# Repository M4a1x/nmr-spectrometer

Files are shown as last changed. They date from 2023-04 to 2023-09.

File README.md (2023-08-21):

<div align="center">
  <a href="" rel="noopener">
 BioNMR Group Logo</a>
</div>

<div align="center">Building a 25MHz NMR spectrometer<br \>01.04.2023 - 30.09.2023</div>

<div align="center">

  []() 
  

</div>

---

<div align="center"> magnETHical is a simple low-cost low-field 0.6T NMR spectrometer based on a RedPitaya and custom hardware. This repository contains everything to build your own. This includes simulations, specifications, full hardware descriptions and CAD designs, Python control code and reproducible measurement results.
</div>

## 📝 Table of Contents
- [📝 Table of Contents](#-table-of-contents)
- [🧐 About ](#-about-)
- [🏁 Getting Started ](#-getting-started-)
  - [✅ Prerequisites](#-prerequisites)
  - [🔧 Hardware](#-hardware)
  - [🖥️ Software](#️-software)
- [⚙️ Running the tests ](#️-running-the-tests-)
- [🧪 Usage ](#-usage-)
- [⛏️ Built Using ](#️-built-using-)
- [✍️ Authors ](#️-authors-)
- [🎉 Acknowledgements ](#-acknowledgements-)

## 🧐 About 
Since the discovery of the Zeeman effect in 1896 and its first use for spectroscopy in the 1940s a lot of technological advancements enabled the capture of increasingly better spectrums and the development of increasingly advanced techniques. Unfortunately, this advancement isn't cheap. Modern NMR spectroscopes cost a fortune, limiting access to this technology to well-funded research institutes, keeping out institutes from the southern hemisphere and limiting its exposure.

magnETHical seeks to provide a low-cost low-field NMR system not only capable of relaxometry but also spectroscopy for a price about an order of magnitude lower than existing devices. It's an open-source well-documented system that can be fully assembled in-house and consists of flexible components that are easily and readily available. 90% of the current ~10k€ price tag is comprised of the magnet with room for at least halving the price in the foreseeable future.

This repository seeks to provide everything needed to order, assemble and operate your own magnETHical NMR spectrometer.

## 🏁 Getting Started 

### ✅ Prerequisites
Great care has been taken to only use widely available free and open-source software so that this project may be built by anyone without any software licensing fees.

Throughout this README and the linked READMEs below a basic familiarity with the used software is assumed. However, anyone with some time on their hands should be able to follow them without much trouble after a very basic introduction to these programs. If you have trouble understanding any of the instructions, please feel free to open an issue - it's likely an error in this documentation and not on your side.

### 🔧 Hardware
The hardware consists of five main parts
- the [magnet](),
- the [digital signal generation, reception and processing board](),
- the [analogue amplification board](),
- the [electrical shimming system]() and
- the [NMR probe]().

Each of these parts can be built, assembled and verified independently of each other. For instructions on building these sub-systems, see the respective READMEs linked in the list above.

With all parts built, the final system needs to be assembled according to the following schematic.

![Block diagram of the different high-level parts of the spectrometer]()

The final assembly then looks something like this

![Picture of the final measurement setup]()

### 🖥️ Software
Having built the hardware above the [Python control software]() can be used to capture spectra. See the linked article for a detailed guide on how to set up the software. We recommend a dedicated computer setup to run the experiments.

## ⚙️ Running the tests 
The simplest test is running marcos test without/with water. measure coil ringing

Explain how to run the automated tests for this system.

## 🧪 Usage 
To record spectra...

How to use the software/hardware. Recomenndations on analysis (Jupyter...)
Add notes about how to use the system.

## ⛏️ Built Using 

- Hardware
  - [KiCAD](https://www.kicad.org/) - ECAD for PCB Design
  - [FreeCAD](https://www.freecad.org/) - MCAD for Enclosures
  - [OpenSCAD](https://openscad.org/) - Parametric CAD for the probe
  - [LTSpice](https://www.analog.com/en/design-center/design-tools-and-calculators/ltspice-simulator.html) - Simulation of electronic circuits
- Software
  - [MaRCoS](https://github.com/vnegnev/marcos_extras) - Low-level control software for the RedPitaya and FPGA
  - [NumPy](https://numpy.org/)/[SciPy](https://scipy.org/)/[Matplotlib](https://matplotlib.org/) - High-level control software and analysis
- Documentation
  - [LaTeX](https://www.latex-project.org/) - Advanced typesetting system
  - [Sphinx](https://www.sphinx-doc.org) - Beautiful documentation

## ✍️ Authors 
- [Maximilian Stabel](mailto:mstabel@student.ethz.ch) - Idea & Initial work including Hardware & Software

## 🎉 Acknowledgements 
- Supervisor
  - [**Takuya Segawa**](https://chab.ethz.ch/forschung/institute-und-laboratorien/LPC/personen/people-details.html?persid=120573) for his supervision and encouragement
- Professors
  - [**Roland Riek**](https://chab.ethz.ch/en/the-department/people/faculty/person-detail.rriek.html) for giving me this opportunity
  - [**Sebastian Kozerke**](https://biomed.ee.ethz.ch/institute/People/person-detail.html?persid=61641) for taking me in as his Master's student
- Support
  - [**Alexander Däpp**](https://ssnmr.ethz.ch/the-group/people/person-detail.html?persid=147372) for his support and patience with the RF hardware
  - [**Tiago Ferreira das Neves**](https://chab.ethz.ch/en/the-department/people/a-z/person-detail.MjU3NzM4.TGlzdC82MDEsLTIxMzAxOTI4MDM=.html) for his electronics support

<div align="center">
  <a href="" rel="noopener">
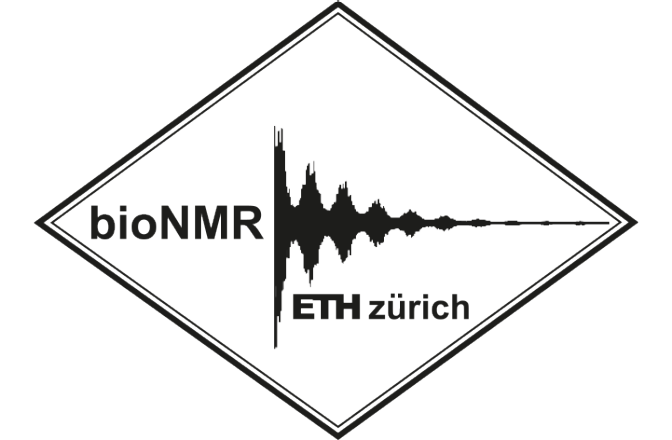
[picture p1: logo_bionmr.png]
BioNMR Group Logo
 </a>
</div>

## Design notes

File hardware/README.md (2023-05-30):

# Workspace

Here lies any code/digital work created during the project. This includes design files, measurement data, photographs and more. This is the main folder to be worked in.

| Folder                                                      | Description                                                                                                         |
| ----------------------------------------------------------- | ------------------------------------------------------------------------------------------------------------------- |
| [`nmr_probe`](./nmr_probe/)                                 | Probe and Probe construction                                                                                        |
| [`marcos`](./marcos/)                                       | MaRCoS software and control of the spectrometer                                                                     |
| [`32-channel_current_source`](./32-channel_current_source/) | Digitally controllable current source for driving the shims                                                         |
| [`tr_switch`](./tr_switch/)                                 | Transmit/Receive Switch for Switching between High-Power RF impulse transmission and low level FID signal reception |
| [`rx_lna_preamp`](./rx_lna_preamp/)                         | Low-Noise Amplifier for the amplification of the FID signal for the RedPitaya                                       |
| [`tx_power_amp`](./tx_power_amp/)                           | Power Amplifier to amplify the excitation pulse of the RedPitaya                                                    |

## General Setup
```text
+------------+                                            +--------------+
|            |     |\            |\                       | RX/TX Switch |
|            |     | \           | \                      |              |
|         TX |-----|  +----------|  +---------------------|---x  \       |         \ | /
|            |     | /           | /                      |       \      |          \|/
|            |     |/            |/                       |        \     |           |
|            |  ZFL-1000+      ZHL-3A+                    |         \    |           |
| Red Pitaya |                                            |          +---|-----------+
|            |                                            |              |
|            |       /|            /|           /|        |              |
|            |      / |           / |          / |        |              |
|         RX |-----+  |----------+  |---------+  |--------|---x          |
|            |      \ |           \ |          \ |        |              |
|            |       \|            \|           \|        |              |
|            |   ZFL-500LN+     PHA-13LN+   PHA-13LN+     |              |
+------------+                                            +--------------+
```

## Previous NMR Work

- Designing and building a low-cost portable FT-NMR spectrometer in 2019: A modern challenge (Alain Lous-Joseph, Philippe Lesot)
- OpenCore NMR (Kazuyuki Takeda)
- LabTools NMR spectrometer based on RedPitaya
- Pavel Demin's NMR spectrometer
- [Simple Low-Cost Tabletop NMR for chemical-shift-resolution spectra measurements](https://www.sciencedirect.com/science/article/pii/S1090780718301745#b0110). Home-built magnet, 60Hz resolution at 2.45MHz (58.8mT), in a later paper down to 1ppm.

## NMR Spectrometer Target Specifications

In addition to the [thesis description/project proposal](../literature/project_proposal/Master_Thesis_Proposal.pdf) we tried to meet the following specifications. This includes design requirements for the physical setup partially repeated in the various sub-sections in the `workspace` directory. Hardware should be reusable. The end goal would be of type "Bring your own Magnet", i.e. a Red Pitaya SDRLab 122.88, our board and magnet should be enough to do spectroscopy, when building their own probes.

- Larmor Frequency: 25MHz (0.6T)
- RF-field strength: x.xx mT
- pi/2 pulse length: x.xx us

> **TODO**
> Write down NMR target specifications here

In the end, separate modules should be developed for ease of reconfiguration. A nice addition would be a single board, including RX/TX amplifiers, switch and filters on one standard [Eurocard 3U (100mm x 160mm x 1.6mm)](https://en.wikipedia.org/wiki/Eurocard_(printed_circuit_board)) FR4 board, so it can be rack mounted, possibly with the common [DIN 41612](https://en.wikipedia.org/wiki/DIN_41612) (~~STEbus~~, VMEbus) connector at the back end. See also the [ARTIQ/Sinara project](https://github.com/sinara-hw/SiLPA_HL/issues/1).

## Red Pitaya SDRlab 122-16 (STEMlab 122-16)
The ADC of the RedPitaya is specified for an RF input voltage of 0.5Vpp. Its absolute maximum rating is 30VDC and 1Vpp RF (~4dBm). This has been verified by looking at the [used ADC](https://www.analog.com/media/en/technical-documentation/data-sheets/218543f.pdf) and the [RedPitaya Schematic](../../literature/instruments/Customer_Schematics_STEM122-16SDR_V1r1(Series1).PDF). Thus the input has to be protected from the power of the transmit cycle.

The easiest way to do this is to use a TVS diode for clamping the input to safe levels. Unfortunately, this severely degrades the ADCs performance according to [this Analog Devices Application Note](../../literature/instruments/rf-samp-adc-input-protection.pdf). The same AN suggests using [RB851Y](https://www.mouser.com/datasheet/2/348/rb851y-209815.pdf) Schottky diodes for ADC input protection
### Basic Specs
|                    |                           |
| ------------------ | ------------------------- |
| Processor          | DUAL CORE ARM CORTEX A9   |
| FPGA               | FPGA Xilinx Zynq 7020 SOC |
| RAM                | 512 MB (4 Gb)             |
| System Memory      | Micro SD up to 32 GB      |
| Console Connection | Micro USB                 |
| Power Connector    | Micro USB                 |
| Power Consumption  | 5 V, 2 A max              |

### RF Inputs
|                                   |                                       |
| --------------------------------- | ------------------------------------- |
| RF input channels                 | 2                                     |
| Sample rate                       | 122.88 MS/s                           |
| ADC resolution                    | 16 bit                                |
| Input impedance                   | 50 Ohm                                |
| Full scale voltage range          | 0.5 Vpp/-2 dBm                        |
| Input coupling                    | AC                                    |
| Absolute max. Input voltage range | DC max 50 V (AC-coupled) 1 Vpp for RF |
| Input ESD protection              | Yes                                   |
| Overload protection               | DC voltage protection                 |
| Bandwidth                         | 300 kHz - 550 MHz                     |

### RF Outputs
|                         |                                  |
| ----------------------- | -------------------------------- |
| RF output channels      | 2                                |
| Sample rate             | 122.88 MS/s                      |
| DAC resolution          | 14 bit                           |
| Load impedance          | 50 Ohm                           |
| Voltage range           | 0.5 Vpp/ -2 dBm (50 Ohm load)    |
| Short circut protection | N/A, RF transformer & AC-coupled |
| Connector type          | SMA                              |
| Output slew rate        | N/A                              |
| Bandwidth               | 300 kHz - 60 MHz                 |

Next Steps:
1. Build 2x Protection diode blocks with 2x BYS-10 schottky diodes each for input protection (limit power to 4dBm/+-0.5V/1Vpp)

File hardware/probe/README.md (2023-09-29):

# NMR Probe

To measure a signal an NMR probe holder is needed that fulfils two tasks:
1. Position the sample correctly in the central homogenous region of the magnet (~6mm diameter sphere)
2. Carry the rf coil for sending and receiving the electromagnetic pulse

To this end, a custom probe for the NMR has to be made.

## Andrew McDowell's NMR probe

### Body

To evaluate the performance (i.e specification) of the magnet, NuevoMRSABR has performed a [crude probe that fits 5mm NMR tubes](../../literature/SABR_Permanent_Magnet_and_Shim/ETH%200.6%20T%20Final%20Report_202301.pdf)

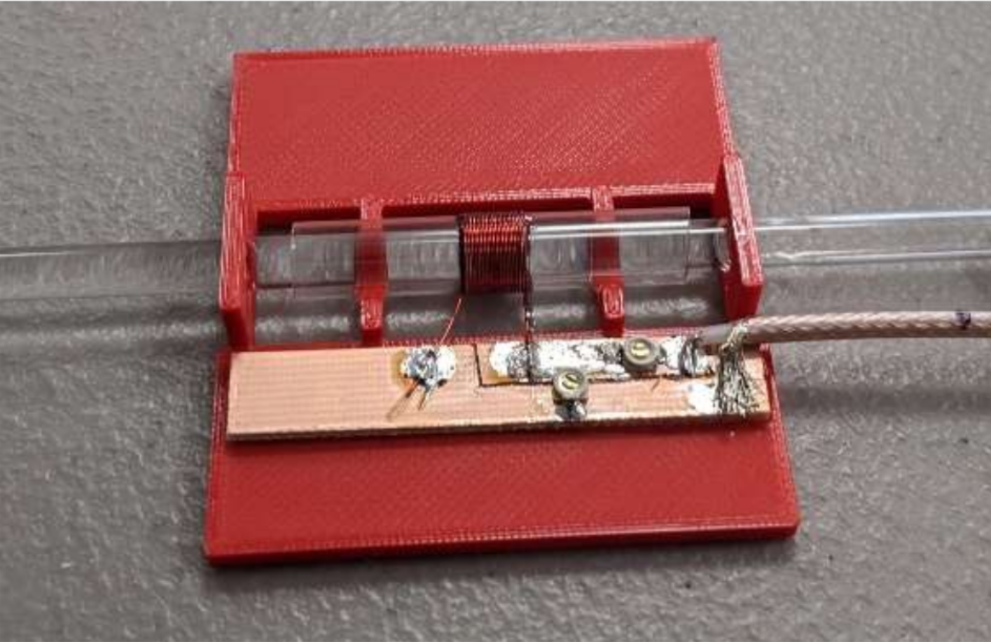
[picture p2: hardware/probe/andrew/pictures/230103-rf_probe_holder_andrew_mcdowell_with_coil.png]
Andrew's Probe


As a first attempt, the same probe holder was 3D printed on a Prusa MK3S MMU2S with 0.3mm PLA on the "DRAFT" setting of the printer in about 26 minutes. The print of which can be seen here:

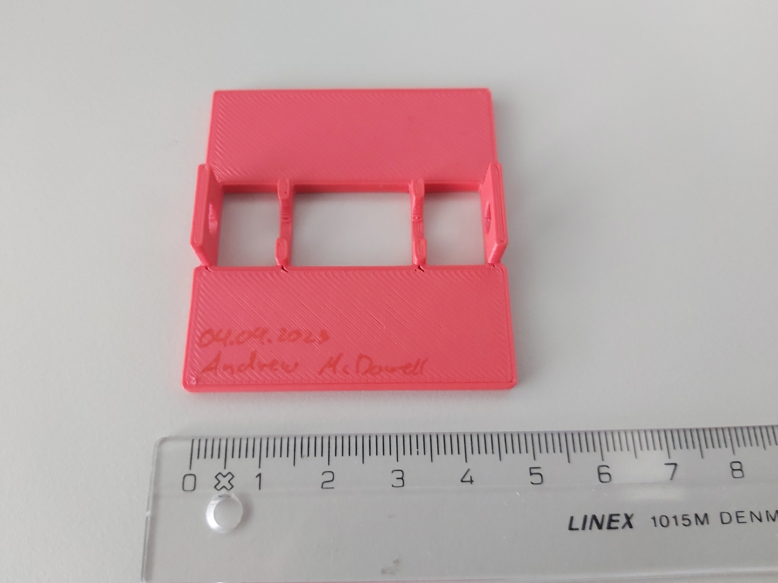
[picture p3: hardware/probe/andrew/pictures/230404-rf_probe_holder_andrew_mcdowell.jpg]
3D Print of Andrew McDowell's NMR Probe holder with Prusa MK3S with 0.3mm PLA


This first print turned out ok, but small gaps can be noticed where the actual tube holders connect to the plates. A smaller print diameter should thus be chosen for the next print.

We then decided that it would be beneficial for the NMR probe to occupy the whole space within the magnet, i.e. to be flush on all sides such that the centre of the is automatically aligned with the centre of the magnet. Andrew's Probe only has dimensions 50mm x 55mm x 9.5mm.

### Coil

The coil consists of approx. ~0.2mm insulated copper wire wrapped around a clear plastic tube in 18 turns on a length of 6mm with a diameter of 7.5mm resulting in a theoretical inductance of 3.00uH when assuming a mu_r of 1 for the inside. Thus expecting an NMR signal from about 8mm long.

Since Andrew sent us his probe we also were able to measure his values, but only inside the circuit (i.e. with tuning and matching capacitances attached) making the results inaccurate. When measured with an PM6303 RCL meter the coil had an inductance of 2.3uH @ 1kHz.

## Probe Holder v1

### Body

Since we only had the *.stl object file of Andrew's NMR probe, the subsequent probe was then redesigned using openSCAD - an open-source solid 3D CAD modeller with its own programming language. [The source](./probe_holder_v1/230403-probe_holder_v1.scad) can be easily modified, parameterized and since it is open-source - easily reproduced.

The design for this first version stayed the same, the probe holder also accepts 5mm tubes and a 7.5mm tube for the coil - merely the outer dimensions have been increased.

The resulting \*.scad file was exported to \*.stl, sliced with Prusa Slicer and printed this time with 0.2mm PLA in about 1.25 hours on a Prusa M3KS printer with the "QUALITY" setting.

The resulting part has exactly the dimensions of the free space of the magnet: 70mm x 83.35mm x 10mm and fits flush inside.
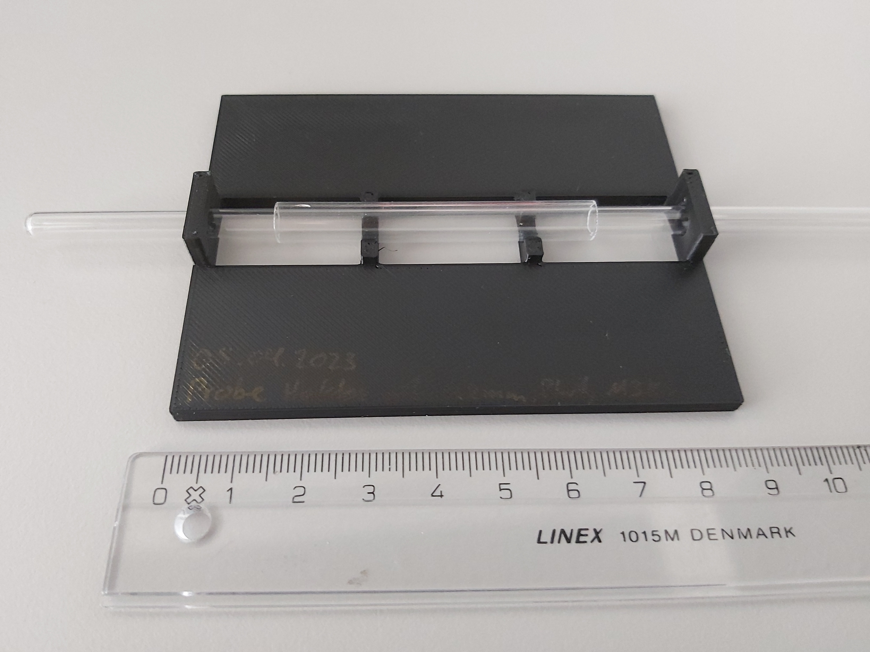
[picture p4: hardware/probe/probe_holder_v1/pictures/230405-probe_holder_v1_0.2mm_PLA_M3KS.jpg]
NMR Probe Holder v1 - 3D printed


### Coil

The coil was wrapped around a 7.5mm glass tube with 0.2mm diameter insulated copper wire on a length of 4mm. With 18 turns this results in a theoretical inductance of 4.5uH. To reach a resonant frequency of 25.01MHz thus a capacitance of 9pF is needed in theory.

When measured with an HP4284 LCR-Meter resting on a styrofoam box we obtained the following measurements:

| Frequency [kHz] | Inductance [uH] | Resistance [Ohm] |
| --------------- | --------------- | ---------------- |
| 0.1             | 0.4             | 0.437            |
| 1               | 5.35            | 0.437            |
| 10              | 3.04            | 0.530            |
| 100             | 2.70            | 0.437            |
| 1000            | 2.74            | 0.627            |

The variability can be explained by stray capacitances of the connection wires, between the individual windings and the surroundings.

To get a better idea of how the coil behaves near the target resonance frequency of 25.01MHz (set by the magnet) a resonant circuit was formed by connecting a 10pF capacitance to both ends. See the bottom coil here:

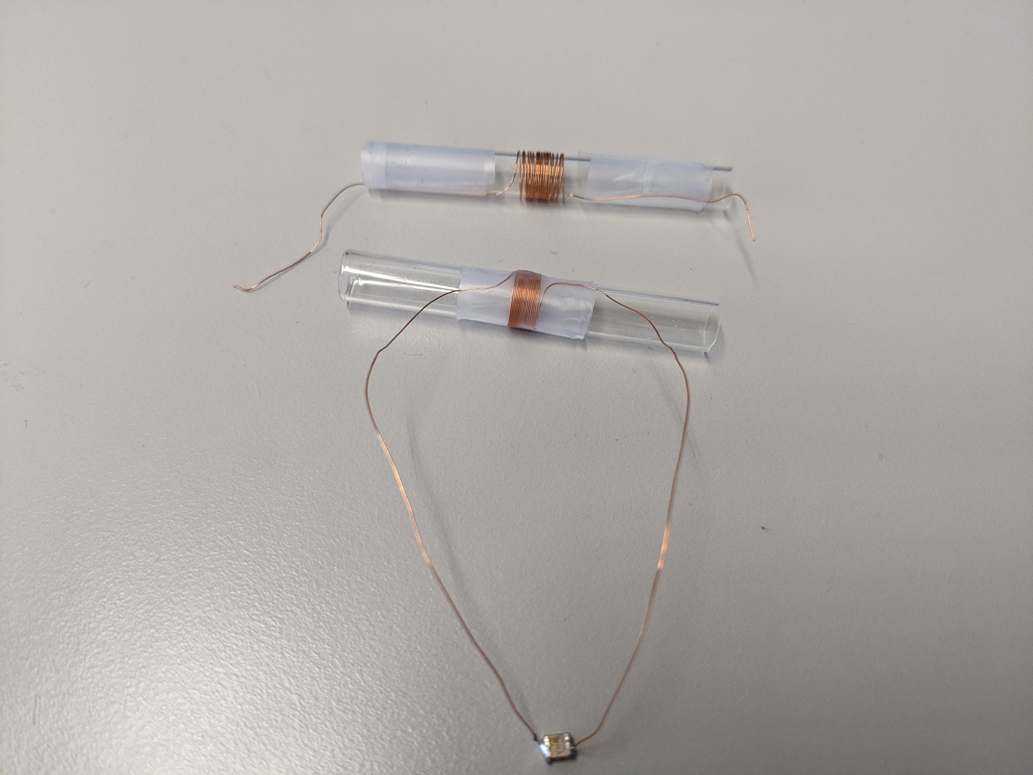
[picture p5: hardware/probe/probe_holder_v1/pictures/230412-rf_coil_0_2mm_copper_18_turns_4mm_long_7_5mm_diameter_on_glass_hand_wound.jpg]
Hand wound coils


The resonant frequency of this setup was then measured with a Rhode&Schwarz ZNB4 vector network analyser (VNA) and a connected pickup coil held near the circuit. We estimated the resonant frequency to be 29.6MHz. With the formula of the resonance frequency of a coil and capacitance of $f_{res} = \frac{1}{2\pi\sqrt{LC}}$ we estimated the inductance to be $L = \frac{1}{4\pi^2f_{res}^2C} = 2.89\textrm{uH}$, which is close to the expected value when looking at the measurements above, but quite far (~35% smaller) from the calculated expectation of 4.5uH.

With this new inductance, the expected capacitance that compensates this inductance is now 14pF. For the tuning capacitance, a variable capacitor with a range of 4.5pF-20pF was therefore chosen (JZ200HV).

A "variable pitch coil" with changing density of windings (tighter at both edges, looser at the centre) could later be investigated for a more homogenous field inside the coil.

## Probe Holder v2

- Reduce loop area of coil leads
- use standard caps in parallel with smaller trimmer cap
- reduce height (v1 has a very tight fit, probably by printing tolerance 0.2mm)
- style after [this OCRA probe from Pier](https://zeugmatographix.org/ocra/2022/04/18/rf-coil-for-the-ocra-tabletop-mri-system/) (also has instructions on build, tuning and matching)
- less turns for larger capacitance for easier tuning an matching
- add rf shielding. Also adds as reference capacitance for a more stable tuning/matching in different surroundings.
- The chosen capacitance range is somewhat too wide. The tune and match procedure is therefore quite inaccurate and difficult.

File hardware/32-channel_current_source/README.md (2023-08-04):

# 32-Channel Current Source

To drive the magnet shims, a 32-channel current source is needed. More details can be found in the [SABR magnet and shim specifications](../SABR_Permanent_Magnet_and_Shim/General%20specifications%20of%20the%20NuevoMR%20shim%20driver%20current%20source.docx)

## Specification
- Price: 320CHF? (10CHF per channel)
- Current: +-500mA
- Voltage: +-2.5V
- Channels: 32
- Programmable
- Isolated

## Noise
The B field is propoertional to the current inside the windings

### Build myself
The premade devices I found are not suitable for low noise, high precision applications as they are often intended for LED dimming through PWM or for lower currents. The self designed supplies on the other hand are too expensive and offer a significantly higher current capability.

The goal of this design is to design a simple, easy-to-understand and modify, circuit from readily available parts with a low per-channel price and acceptable performance. It should be easy to build as well, ideally through hand soldering (i.e. no BGA/QFN chips)

Since I'm doing a basic linear regulation, the maximum voltage drop across the coil will be U = R * I = 1 Ohm * 500mA = 0.5V. The remaining power needs to be dissipated inside the supply. A power dissipation of ~1W-1.2W is acceptable in a mosfet/opamp without much consideration for heat management (see Infineon AN-2021-02, D2PAK, 0.5A, max. dT = 74K). Thus the maximum voltage drop over the regulator is U = P / I = 1W / 500mA = 2V. Therefore the power supply should be around 2.5V, maximum 2.9V, if everything is dissipated in a single device. Generally, the supply voltage should be chosen as low as possible.

- Red Pitaya SPI -> 32 DACs
- Simple OpAmp current source circuit (Tietze & Schenk)
- I found the [Howland current pump](https://www.ti.com/lit/an/snoa474a/snoa474a.pdf). This seems to be an option, but also poses high requirements on the resistor selection, is relatively complex to analyze and slow.
- [Martinos Lab](https://rflab.martinos.org/index.php?title=Current_driver:Current_driver) uses two opamps (OPA549, ~30chf) per channel in a push-pull configuration. There are several papers with an almost identical setup. e.g. [Bidirectional, Analog Current Source Benchmarked with Gray Molasses-Assisted Stray Magnetic Field Compensation](https://www.mdpi.com/2076-3417/11/21/10474?type=check_update&version=1)
- [A PI feedback control would also be an option](https://pubs.aip.org/aip/rsi/article/90/1/014701/368287/Ultra-low-noise-and-high-bandwidth-bipolar-current). This probably requires more tuning as the control loop is bigger, more parts and slower regulation.
- There's a comparison of the two MRI gradient boards on [MaRCoS wiki](https://github.com/vnegnev/marcos_extras/wiki/dacs)
- Get inspiration from the [OCRA1 Gradient board](https://zeugmatographix.org/ocra/2020/11/27/ocra1-spi-controlled-4-channel-18bit-dac-and-rf-attenutator/) (i.e.based on [this DAC (AD5781, 18bit 30€)](https://www.analog.com/media/en/technical-documentation/data-sheets/AD5781.pdf))
- Get inspiration from the Gradient Board [GPA-FHDO](https://github.com/menkueclab/GPA-FHDO) (uses the same architecture and parts as Martinos Lab above, i.e. OPAMP OPA549 (25chf) in push-pull config, input noise density 70nV/sqrt(Hz), current noise density 1pA/sqrt(Hz))
- Modular Design Example: [32 channel rf signal amplifier](https://www.opensourceimaging.org/project/32-channel-rf-receive-chain-amplifiers/)
- Probably need output filter (e.g. to prevent 60Hz noise)
- DAC:
  - For practicality reasons at least 4 channels per device are desirable so no MUX chip is needed for both I2C or SPI (daisy-chain). Prices steeply increase above 8 channels, with 8 channels usually being the cheapest per channel.
  - To get a resolution of 0.1mA at least 14bit are necessary. While 12-bit devices are significantly cheaper, the difference between 14 and 16-bit seems negligible. Thus a 16-bit device is chosen.
  - MCP4728 (4ch, 12bit, 2.25chf [0.562chf per channel], ridiculously cheap for some reason)
  - MCP48 (4ch, 12bit, 6.75chf [1.67chf per channel])
  - MCP47 (8ch, 12bit, 11chf [1.375chf per channel])
  - DAC80501 (1ch, 16bit, same as in Martinos/GPA-FHDO) ~6CHF on mouser.ch
  - DAC8555 (4ch, 16bit, 12.40CHF [3.1chf per channel], ext. ref, no daisy-chain)
  - DAC8568 (8ch, 16bit, int. ref, no daisy-chain)
  - DAC80508 (8ch, 16bit, ~21CHF [2.6chf per channel], QFN!)
  - **AD5676/AD5675 (R suffix with internal reference) (8ch, 16bit, ~20CHF [2.5chf per channel], TSSOP)**
- Voltage Reference:
  - See [TI's Voltage Reference Selection Guide (2015)](https://www.ti.com/lit/ml/snvd001a/snvd001a.pdf)
  - LM4041 1.225V fixed (100ppm/K drift, 0.1% initial acc., shunt, 0.5chf)
  - REF5025 (3ppm/K, 0.05% initial acc., series, 3CHF)
  - LM4140 (3ppm/K, 0.1% initial acc., series, 5CHF)
  - Higher Precision Reference REF01
- OpAmp
  - Power (I>=1A):
    - **NCS2372/NCV0372B/TCA0372 (dual, 1.35CHF)**
    - **L2720W/L272/L272D (dual, 2.70chf, identical to tca0372, better datasheet)**
    - OPA547 (1ch, 10chf)
    - OPA551(6chf, 200mA)
    - OPA2675 (dual, 3.37chf, QFN)
    - in Andrew/Conradi Paper: OPA025 (not found. maybe opa2544? 25chf), 0.5ohm current sense low side
  - Rail2Rail
    - **LMV358/LMV324 (Low Voltage)**
    - TLV904x (Ultra Low Voltage)
    - TLV9104 
- Audio Amp
  - LM1877 (dual, 1.5CHF)
- Supply: Linear regulator Dual LM317
  - Optional: Make precision by using TL431 reference (see eevblog)
  - REF01 for higher precision alternative
- Power Resistor: 1x WSC25155R000FEA (5 Ohm, 1W, 1%, 50ppm/K, 1CHF)

### Use LED current driver
- TL4242 (500mA, +-5%)
- HV9961 (+-3% current accuracy)
- NCR320PAS (250mA only)
- STCS05A (0.5A with a ±10% precision)
- TLD1211SJ (only up to 85mA)
- LM8040 (PWM controlled, accuracy?)
- LT3092 (200mA max)
- BCR420 (+-10%)

### Use current driver IC
- Device Power Supply IC (MAX32010, acc. 0.15%, 50€ pp)

### PCB Shape
was made with FreeCAD. Use the 3D step model by Hammond (in the 3dmodels folder) and open it in FreeCAD
- Use the KiCADStepUp Workbench AddOn
- Select the PCB that is inside the enclosure (remember to turn off step unification before import to get separate parts)
- First convert it two 2D ith the corresponding button
- Then convert the 2D shape to a Sketch with the corresponding button
- Export the Sketch to dxf (or svg) and import it in KiCAD on the Edge.Cuts Layer. No need to constrain the Sketch, though it is possible using the PDF with the measurements you can download from the Hammond website

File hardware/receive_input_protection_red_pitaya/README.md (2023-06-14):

# Red Pitaya Input Protection

The LNAs on the receive chain will amplify any signal leaked by the RF switch. The LNAs themselves are therefore protected with BAV99 diodes that clamp the voltage to roughly ~+8dBm (~1.5Vpp) and up to +10dBm (2Vpp). The input power limit for continuous waves of the PHA-13LN+ amps is +8dBm for continuous waves and +21dBm for up to 5min. Unfortunately, these specs are too high for the RF inputs of the Red Pitaya which are specified to a max of 0.5Vpp for the ADC sampling and a maximum of 1Vpp without damaging the inputs. Thus instead of using the BAV99 silicon switching diodes, diodes with a lower forward voltage - such as Schottky diodes - have to be used. Simply choosing a general-purpose Schottky diode - the BYS10 in this case - led to a high attenuation of the signal of a measured ~10dB. As seen in the simulation - which agrees very well with the measurement results - a large phase shift occurs. This leads us to believe that a high capacitance forming a low pass filter with the 50 Ohm load input is responsible for the attenuation of the signal. Through a parameterized search and a SPICE simulation, the RB520SM-30 was chosen as a suitable Schottky diode with low enough capacitance and other losses, that can clamp the maximum output power of the PHA-13LN+ of about +24dBm to about +1Vpp thus even in the case of high power leaking through the TX/RX switch, the Red Pitaya input is still protected.

For details see the [`clamping_diodes.asc`](./clamping_diodes.asc) LTSpice Simulation for the results for the mentioned diodes as well as other investigated ones.

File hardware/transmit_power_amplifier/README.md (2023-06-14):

# TX Power Amplifier
Transmit power is expected to be in the area of Watts (Louis-Joseph and Leot (2022)). The maximum TX power of the Bruker Fourier 80 Benchtop spectrometer is 5W (37dBm) (through E-mail correspondence) and the [OpenCore NMR uses 1W TX power](https://www.sciencedirect.com/science/article/pii/B9780080970721000078?via%3Dihub) with a 2mm diameter tube as well. The maximum output power of the RedPitaya is -2dBm or 0.5Vpp thus a gain of 32dB to 39dB (to reach 1W or 5W respectively) would be required. A single amplifier with this gain and power output is not readily and cheaply available. Therefore a multi-stage approach is preferable.

## Previous Work/Inspiration
- The [NPTB00004A](https://www.mouser.ch/datasheet/2/249/NPTB00004A-1109174.pdf) (5W/37dBm, gain 23dB @900MHz, 70% efficiency, DC-6GHz, 20€) found on mouser, used in [ARTIQ/Sinara Booster (see below)](https://github.com/sinara-hw/Booster/releases) as well which uses an [ADL5535](https://www.mouser.ch/datasheet/2/609/ADL5535-3120463.pdf)/[ADL5536](https://www.mouser.ch/datasheet/2/609/ADL5536-3120503.pdf) (20MHz-1GHz, gain 16dB/20dB, 5€) then a [PHA-1+](https://www.minicircuits.com/pdfs/PHA-1+.pdf) (50MHz-6GHz, gain 17dB, P1dB 22dBm, 3€) as preamps
- The [2SK3475](https://www.mouser.ch/datasheet/2/408/2SK3475_datasheet_en_20070219-3106972.pdf) (P0 630mW, 2€) and [2SK3476](https://www.mouser.ch/datasheet/2/408/2SK3476_datasheet_en_20140301-3106903.pdf) (P0 7W, 5€) RF transistors (MOSFET, N Channel) as used in this [The Stone Zone blog post](http://thestone.zone/radio/2021/06/05/power-amplifier.html) seem to be a good option for a few Watt amplifier
- The IRF510 is (ab-)used by a lot of HAM radio enthusiasts for TX amplifiers in the 10m - 20m bands (30MHz - 15MHz).
  - [The Stone Zone Blog post about using an IRF510 Mosfet with a 2n2222 push-pull preamp](http://thestone.zone/radio/2020/12/13/multi-watt-amplifier.html) for a few Watt amplifier (up to 12W?).
  - [Here's a KiCAD board on GitHub with the IRF510](https://github.com/paulh002/IRF510-rf-amplifier).
  - [Another KiCAD project here](https://github.com/thaaraak/IRF510-Amplifier-v2) with a [circuit walkthrough on YouTube](https://www.youtube.com/watch?v=D4UhOmum_oU) as well.
  - [HAM Radio Amplifier based on IRF510](https://github.com/kholia/HF-PA-v6), [another project based on the same transistor](https://github.com/paulh002/IRF510-rf-amplifier)
- [JQI AOM Amp](https://github.com/JQIamo/aom-driver) used a ZHL-2-8+ (535€) or a ZHL-3A-4+ (~239€) or a [ZHL-5W-1+](https://www.minicircuits.com/pdfs/ZHL-5W-1+.pdf) (~1500€). [There's a paper as well](https://github.com/JQIamo/aom-driver/blob/master/aom_driver.pdf). Here they use a [HMC1099](https://www.analog.com/media/en/technical-documentation/data-sheets/hmc1099.pdf) (gain 18.5 dB, P4dB 40dBm, noise 8dB, 120€) power amp. Datasheet includes typical application and evaluation PCB. Separate repo for [the GaN amplifier](https://github.com/JQIamo/GaN-Amplifier) they used alternatively. Preamp is a [HMC8410](https://www.analog.com/media/en/technical-documentation/data-sheets/hmc8410.pdf) (gain 19dB, P1dB 21 dBm, noise 1.1dB, ~50€).
- The [2SCR573](https://fscdn.rohm.com/en/products/databook/datasheet/discrete/transistor/bipolar/2scr573d3tl-e.pdf) Power transistor (BJT, NPN) seems like a good alternative to the IRF510 used above as used in these preliminary tests in [The Stone Zone blog](http://thestone.zone/radio/2022/12/20/2sc573-testing.html)
- The [PHA-202+](https://www.minicircuits.com/pdfs/PHA-202+.pdf) (30MHZ-2.7GHz, gain 18dB, P1dB 28 dBm, noise 3dB, 14€) was used in a [design in the ETH Quantum Optics Group](https://www.changpuak.ch/electronics/PHA-202+Amplifier.php). It seems to work well down to 2MHz despite the datasheet characterization starting at 30MHz. The design is very simple since the chip doesn't need any complex surrounding circuitry. Unfortunately, it doesn't quite reach the desired output levels of 30-37dBm. The design includes specifics for the heatsink, case and PCB. I originally found the chip in the [ARTIQ/Sinara SiLPA discussion](https://github.com/sinara-hw/SiLPA_HL/issues/1), where it was well-evaluated for its capabilities and ease of use, but there were concerns about temperature stability and lack of power. In the end, they went with the [QPB8808](https://www.qorvo.com/products/p/QPB8808) (50MHz-1.2GHz, gain 20dB, P1dB +33dBm, noise 4.5dB, ~29€) CATV (Cable Television) amplifier. Since CATV works on 75 Ohm impedance it needs a 1.5:1 balun at the input and output. A stripped-down version could be a valid option although the specified frequencies are too high - it might still work. Uses an ADL5536 and a PHA-1+ as preamps (same as Sinara Booster above)
- [Martinos Tabletop MRI](https://tabletop.martinos.org/index.php?title=Hardware:RF) TX line uses a 1.2W [ZHL-3A+](https://www.minicircuits.com/pdfs/ZHL-3A.pdf) power amplifier (gain 25dB, P1dB 32 dBm, 5dB noise, ~300€), which they had to gate due to the carrier frequency coming through
- [In this Halbach MRI Magnet Project that also uses MaRCoS](https://pure.tudelft.nl/ws/portalfiles/portal/150811992/NMR_in_Biomedicine_2023_Obungoloch_On_site_construction_of_a_point_of_care_low_field_MRI_system_in_Africa.pdf) a [ZX60-100VH+](https://www.minicircuits.com/WebStore/dashboard.html?model=ZX60-100VH%2B) (0.3-100MHz, max power: 1W/30dBm, gain 36dB, P1dB 30dBm, noise 4dB, ~350€) was used (they also used a passive TR switch based on crossed diodes and lambda/4 pi circuit)
- [The FOSS 2019 paper (Louis-Joseph and Lesot)](../../literature/related_projects/foss_nmr_spectrometer_15MHz.pdf) sends 37dBm max using a ZHL-5W-1 (gain: 46dB, max 40dBm, noise 4dB, ~1500€)
- The [OCRA Project uses a ZFL-500HLN+](https://www.minicircuits.com/pdfs/ZFL-500HLN.pdf) (gain: 20dB, noise: 3.8dB, P1DB: 17dBm, ~150€)
- The [MAGX-011086A](https://cdn.macom.com/datasheets/MAGX-011086A.pdf) GaN power amplifier (gain 24.6dB @ 900MHz, 37dBm max, has a typical application circuit I could reproduce (4W) (~20€)
- The [PHA-13HLN+](https://www.minicircuits.com/pdfs/PHA-13HLN+.pdf) (gain 24dB, P1dB 27.3dBm, noise 1.1dB) has a maximum power of 28.7dBm typically (~0.5W)
- [NPA1003](https://media.digikey.com/pdf/Data%20Sheets/MA-Com%20Technology%20PDFs/NPA1003.pdf) 38dBm power amplifier, 50ohm matched

## Background
- [Interesting general article about RF Power amps in NMR](http://www.cpcamps.com/introduction-to-nmr-mri-amplifiers.html)
- [IEEE Paper on how to build an RF power amp for NMR (10-25MHz)](https://ieeexplore.ieee.org/document/5163353)
- [OpenCore NMR](https://reader.elsevier.com/reader/sd/pii/S1090780708000670?token=C091614A806EFA2BEE0FBD33618073B2E48461C188AAA27B69640A102C862D004694C98189A10EBBDE6AD556E4D1E2EC&originRegion=eu-west-1&originCreation=20230510092722) uses a low pass filter  after the DAC to get rid of unwanted image frequencies due to the digital stepping through the waveform
- The [ARTIQ/Sinara Booster](https://github.com/sinara-hw/Booster/wiki) looks like a good inspiration
- The [ARTIQ/Sinara SiLPA](https://github.com/sinara-hw/SiLPA_HL/issues/1) as well
- More FM transmitter circuits on [electroschematics.com](https://www.electroschematics.com/diy-fm-transmitter-circuits/)
- [NSP AN721 on Impedance Matching for RF Power Transistors](https://www.nxp.com/docs/en/application-note/AN721.pdf)
- [STM RF Board Layout Guide](../../literature/rf/an5407-optimized-rf-board-layout-for-stm32wl-series-stmicroelectronics.pdf)

## Discussion
The cheapest option with the highest power output which is still relatively easy to build based on the above findings would be a design based on the RF transistors 2SK3475 (16dB, 2€) and 2SK3476 (11dB, 5€), which unfortunately seem to be obsolete. To get to 39dB amplification needed, another 12dB would be needed. Again the ADL5535 (16dB) could be used for that? probably in conjunction with a 3dB pi attenuator (see e.g. Booster schematic)

The next option would be using the PHA-202+ amplifier (18dB, P1dB 30dBm, 14€) with a preamplifier, e.g. the ADL5535 (16dB, P1dB 17.7dBm, 5€)/ADL5536 (20dB, P1dB 18dBm, 5€, probably too close to the P1dB coming from -2dBm) or PHA-1+ (17.2dB, P1dB 21.5dB, 3€) from Booster or the GALI-74+ (25dB, P1dB 19dBm, 3.50€). This would be slightly simpler as we'd be using a finished amp and preamp, but would have less max. power (~1W). Going with 18dB + 20dB (PHA-202+ and AD5536) we'd get 38dB gain on a -2dBm signal, thus 36dB which would make a 6dB pi attenuator in between feasable, as well as an input bandpass pi/t filter.

The last option would be using the NPTB00004A transistor (23dB) together with the ADL5535 (16dB) to reach 39dB, basically a stripped-down Booster.

There are a lot of options for preamplifiers though, e.g. a QPA4586A, QPA7489 would probably work as well even (but their specified range is rather large compared to the ADL5535/6). They are roughly the same price (~4€).

The two RF transistors of the first option are not recommended for new designs and the PHA-202+ option only reaches 1W output power. The last option also consists of a power transistor requiring its own bias, supply and matching calculations. Thus the simplest first step would be to build the PHA-202+ with a preamp. In a further step, the PHA-202+ could be replaced either with the QPB8808 as in SiLAS which wouldn't require any special calculations, but matching of 75 to 50 Ohm or a self-designed amplifier based on a transistor.

[Building my own amplifier](https://w3axl.com/?p=308) based on the transistors with correct power supply, biasing and input/output matching networks [or matched feedback networks](http://www.w1ghz.org/small_proj/Simple_Broadband_Power_Amplifiers.pdf) would probably need more time and research.

## Conclusion
1. Buy ZHL-3A+ power amplifier
2. Buy a SCLF-27+ filter for output filtering
3. Design board based on PHA-202+ and ADL5535 for 1W PA
4. Design own power amplification stage using an RF transistor, e.g. NPTB00004A

## Additional Stuff
Should be able to power off the poweramp when not transmitting. This could simple be done like in the power amp from martinos lab with a pnp/npn bjt transistor combination [probably taken from here](https://electronics.stackexchange.com/questions/248946/high-side-switching-12v-with-bjt-mosfet) or a npn/p-mosfet combination like [in this stackoverflow answer](https://electronics.stackexchange.com/questions/606733/why-use-both-a-bjt-and-a-mosfet-for-switching-a-subcircuit) or [this one](https://electronics.stackexchange.com/questions/407303/how-to-drive-p-channel-mosfet)

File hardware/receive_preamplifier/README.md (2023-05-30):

# RX LNA Preamp

This folder contains the first amplifier in the RX chain, based on the [design of Martinos RF Lab](https://rflab.martinos.org/index.php?title=Low-noise_RF_Preamplifier) with the [PHA-13LN+](https://www.minicircuits.com/pdfs/PHA-13LN+.pdf) chip from mini-circuits.

This design could easily be adapted to be included in an all-in-one board including an RX preamplifier, RX amplifier, TX amplifier, TX power amplifier and TX/RX switch.

The design was adapted using the newest KiCAD version (7.0.2, 12.05.2023).

## Specifications
The receive amplifier needs to amplify the signal from uW level (~-30dbm, [Louis-Joesph and Lesot (2022)](../../literature/related_projects/foss_nmr_spectrometer_15MHz.pdf)) to around -2dbm (~0.5V @ 50Ohm) for the 16-bit ADC of the RedPitaya. Thus a gain of at least 28dB is needed. Previous work (see below) uses either a two or even three-stage design.

Furthermore, the design should be simple and easily reproducible. At best, it should be hand-solderable, without the need for a reflow oven or hot air gun. The parts should be easy to obtain and a low part count would be desirable as well. The target/carrier frequency is at 25MHz corresponding to the 1H Larmor frequency of the 0.6T magnet we're using.

One option would be to use an amplifier chain similar to [Martinos (MIT) lab](https://rflab.martinos.org/index.php?title=Main_Page) used in their MRI experiments for the reception. This consists of three stages, two PHA-13LN+ (~20€/eval board ~140€) and one ZFL-500LN+ (~125€). Sometimes the RX LNAs are already integrated into the T/R Switch - e.g. the [T/R Switch from Menküc](https://github.com/menkueclab/TR-Switch) uses the two PHA-13LN+ LNAs based on the design from Martinos lab. Since the maximum output level of the PHA-13LN+ is sufficiently high three PHA-LN13+ could be used as well.
> **TODO**
> Experimentally verify that 40dB (vs the 30dB estimate) are suitable for us, or if we need more/less amplification.

## Previous Work/Inspirations
- [Martinos Lab](https://rflab.martinos.org/index.php?title=Low-noise_RF_Preamplifier) uses a 3-stage design for their low-noise RF preamplifier. It consists of two PHA-13LN+ (Gain: 24dB, P1dB: 23dBm, Noise: 0.9dB @20MHz/5V) and one ZFL-500LN+ (Gain: 28dB, P1dB: 8dBm, Noise: 2.9dB, @5MHZ/15V) at the end before going into the measurement equipment. The two PHA-13LN+ are protected by BAV99 signal switching diodes (Vf=~0.7V), clamping the power at ~7dBm (PHA-13LN+ max. input pulse: 21dBm)
- The [tabletop MRI by Martinos Lab](https://tabletop.martinos.org/index.php?title=Hardware:RF) uses a 2-stage amplifier based on the [Gali-74+](https://www.minicircuits.com/pdfs/GALI-74+.pdf) (~4€/eval board 160€). (25dB gain, P1dB 19dbm, 2.7dB noise). Which is cheaper with comparable gain, but a higher noise figure. The RF-Switch uses [BYS-10](https://www.vishay.com/docs/86013/bys10.pdf) Schottky diodes with a V_f of 0.5V (-2dBm) for protection.
- [Hibino](https://www.sciencedirect.com/science/article/pii/S1090780718301745#b0110) used a CA-251F4 preamplifier (DC-10MHz, voltage 40dB gain, output power +-10mA max) which is unsuitable for our frequencies. They also used an AD603 variable preamplifier as their third 30dB variable gain input stage.
- The ZFL-500LN+ from mini-circuits has a gain of almost exactly 28dB when powered with at least 15V, with a P1dB of 8dBm over its whole specified range. Its noise figure is typically 2.9 dB.
- The [EasySDR](https://github.com/IgrikXD/Easy-SDR) uses a [PSA4-5043+]() or a [PGA-103+]() protected by BAV99 as well for their LNA. Optionally with a FV1206 or GE0805C-3 high-pass filter.

## Filters
- The [T/R-Switch by Menküc](https://github.com/menkueclab/TR-Switch) uses a low-pass filter at the output of the LNA chain, in our case this could be e.g. [SCLF-30+](https://www.mouser.ch/datasheet/2/1030/SCLF_30_2b-1701154.pdf) (~19€), [SCLF-27+](https://www.mouser.ch/datasheet/2/1030/SCLF_27_2b-1701261.pdf) (~13€/eval board 120€), or a custom design bessel/butterworth/... Should be a lowpass, since all other possibly interesting atoms have a lower resonant frequency than a single 1H.

## TODOs
- [ ] Experimentally verify the PHA-13LN+ boards I made
- [ ] Experimentally verify if a filter is needed/useful
- [ ] Design my own filter (cheaper!)
- [ ] Based on the above results make a filter (breakout) board
- [ ] Integrate together with own T/R Switch and TX amplifiers on one board

## Conclusions
1. Buy 1x PHA-13LN+ evaluation board
2. Buy 1x SCLF-27+ evaluation board
3. Build 3x PHA-13LN+ individual gain blocks based on Martinos Lab Design
4. Build 2x protection diode blocks with a BAV99 dual-diode each for the evaluation boards
5. Build 1x protection diode blocks with BYS-10 Schottky diodes for the RedPitaya inputs

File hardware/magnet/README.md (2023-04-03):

# Permanent Magnet and Shim

- [Final Report](./ETH%200.6%20T%20Final%20Report_202301.pdf.pdf)
- [Plan of the Magnet](./105490_12mmGap_EEC_0.6T_CHECK_PRINT_8_25_2022.PDF)
- [Details of the Shim control](./2023-01-03%20ETH%200.6T%20active%20shim%20Matrix%20and%20Pinouts.xlsx), [connector parts](./Connector_details_shim_drivers_Andrew_McDowell_20221205.docx) and [shim driver specifications](./General%20specifications%20of%20the%20NuevoMR%20shim%20driver%20current%20source.docx)

Provided by SBAR and NuevoMR (Andrew McDowell)

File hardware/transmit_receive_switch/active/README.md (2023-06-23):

# TX/RX Switch

The T/R Switch needs to handle  ~5W, max 10W in transmit power (Bruker max. 5W!). Two main options exist:
- passive T/R Switch (lambda/4 + passive diodes) as built by Alex. Possibly change the Diodes to Schottky diodes for smaller leak-through power. Why aren't we using PIN diodes?
- active T/R switch (lambda/4 + pin diode)
  - built from discrete components, e.g. 
    - [this Github by Menküc](https://github.com/menkueclab/TR-Switch), explained in  [this Infineon AN](https://www.infineon.com/dgdl/Infineon-AN_1809_PL32_1810_172154_PIN%20diodes%20in%20RF%20sw%20applications-AN-v01_00-EN.pdf?fileId=5546d46265f064ff016643e2bc241042))
    - [OCRA T/R Switch](https://zeugmatographix.org/ocra/2021/09/30/transmit-receive-switch-for-the-ocra-tabletop-mri-system/) (PIN Diodes ~2CHF)
  - commercial chip, e.g. 
    - [QPC6324](https://www.mouser.ch/datasheet/2/412/QPC6324_Data_Sheet-1265756.pdf), 31dBm term. CW
    - [HMC849A](https://www.analog.com/media/en/technical-documentation/data-sheets/hmc849a.pdf), 33dBm CW through, 26.5dBm term. CW (thermal), absorptive
    - [HMC8038](https://www.analog.com/media/en/technical-documentation/data-sheets/HMC8038.pdf), 30dBm term. CW, 100MHz - 6GHz
    - [RFSW6024](https://www.qorvo.com/products/p/RFSW6024), 28dBm term max. CW driven simultaneously
    - [PE42553](https://www.psemi.com/pdf/datasheets/pe42553ds.pdf), 10us, power on: 36dbm CW/39.5dBm pulsed, terminated: ~30.5dBm pulsed (est.)/28dBm CW
    - [PE42020](https://www.psemi.com/pdf/datasheets/pe42020ds.pdf) max 26dBm CW term.
    - [PE42520](https://www.psemi.com/pdf/datasheets/pe42520ds.pdf) 26dbm term. CW
    - [HMC1118](https://www.analog.com/media/en/technical-documentation/data-sheets/HMC1118.pdf), 28dBm term. CW
    - [HMC544A (reflective)](https://www.analog.com/media/en/technical-documentation/data-sheets/hmc544ae.pdf) (5W) used in Sinara Booster
    - [Skyworks SKY12208 PIN Diode Switch](https://www.skyworksinc.com/-/media/SkyWorks/Documents/Products/601-700/SKY12208_478LF_201671D.pdf) 50W, reflective?
    - [MASW-000932](https://www.mouser.ch/datasheet/2/249/MASW_000932-838129.pdf) [MASW-000932](https://cdn.macom.com/datasheets/MASW-000936.pdf) (max 80W/120W), requires high bias voltage?, reflective
    - [HMC874A](https://www.analog.com/media/en/technical-documentation/data-sheets/hmc784a.pdf), reflective, P0.1dB 36dBm, 30dB Return loss, 100ns
    - [MASWSS0178](https://www.mouser.ch/datasheet/2/249/MASWSS0178-318572.pdf), P1dB 29dBm, 24ns, absorptive, 
    - (also see [DigiKeys Antenna Switching Note](https://www.digikey.ch/en/articles/how-to-quickly-safely-switch-antenna-transducer-transmit-receive-modes) or [Digikeys RF Switch Note](https://www.digikey.de/de/articles/choosing-an-rf-switch))
    - [20CHF Commercial RF Switch](https://www.mikroe.com/rf-switch-click) used in [SiLPA](https://github.com/sinara-hw/SiLPA_HL/issues/1)
    - [Mini circuits packaged SPDT active switch ZX80-DR230-S](https://www.mouser.de/ProductDetail/Mini-Circuits/ZX80-DR230-S+?qs=A6eO%252BMLsxmSxGVKhwBQ6Xg%3D%3D&_gl=1*166vu6r*_ga*dW5kZWZpbmVk*_ga_15W4STQT4T*dW5kZWZpbmVk*_ga_1KQLCYKRX3*dW5kZWZpbmVk)
    - [MSWA2-50+](https://www.minicircuits.com/pdfs/MSWA2-50+.pdf), [MSWA-2-20+](https://www.minicircuits.com/pdfs/MSWA-2-20+.pdf), too low P1dB (<20dBm)
    - ~~[M3SWA-2-50DR up to 20dBm](https://www.minicircuits.com/pdfs/M3SWA-2-50DR.pdf) used by OpenCoreNMR for pulse modulation~~
  
[Typical leakages are 30mVpp for GaAs switches and 300mVpp for PIN diode based switches](https://www.minicircuits.com/app/SW13-2.pdf) (so ~10dB better). This AN also states that PIN Diodes can be used with frequencies >10MHz (GaAs down to DC) and are mainly limited by average power dissipation. GaAs is limited by peak voltage and current ratings inside the GaAs transistors. GaAs is faster.

For simplicity of use, a passive switch would be advantageous if possible. The passive solution should leak only a little power that can be clamped by the protection diodes before the amplifier. This has the advantage that we can see the ringing of the coil and accurately start measuring after it ringed down?

Next steps:
1. For now Alex' amplifier can be used the 6dBm output power that leaks from input to output can be clamped at every stage of the amplifier chain.
2. Since we don't have that much power the design could probably be made smaller, e.g. only one lambda/4 filter instead of three
3. Use Schottky Diodes instead of normal signal switching diodes for a lower power leak
4. A switch

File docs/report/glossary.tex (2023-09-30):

% used with \gls
\newglossaryentry{computer}{
    name=computer,
    description={is a programmable machine that receives input, stores and manipulates data, and provides output in a useful format}
}
\newglossaryentry{MRlbl}{
    name=Magnetic Resonance,
    description={is a phenomenon where atomic nuclei in a strong constant magnetic field, excited by a second oscillating magnetic field of correct frequency resonate and emit a corresponding electromagnetic signal}
}
\newglossaryentry{NMRlbl}{
    name=Nuclear Magnetic Resonance spectroscopy,
    description={is a spectroscopic technique to observe shifts in magnetic field strengths in atomic nuclei. Or in simpler terms a \href{https://blogs.bath.ac.uk/csct/2016/hidden-force-looking-machine/}{Hidden Force Looking Machine}}
}
\newglossaryentry{CW-NMRlbl}{
    name=Continous Wave Nuclear Magnetic Resonance spectroscopy,
    description={is an \gls{NMRlbl} experiment performed by slowly varying the excitation frequency and observing the resonance behaviour of nuclei inside the sample}
}
\newglossaryentry{FT-NMRlbl}{
    name=Fourier Transform Nuclear Magnetic Resonance spectroscopy,
    description={Instead of slowly varying the frequency as in \gls{CW-NMRlbl}, a single pulse of a given length with a fixed frequency is sent. According to Fourier's theory, this \enquote{smears} the frequency and excites nuclei with different resonant frequencies simultaneously}
}
\newglossaryentry{BNClbl}{
    name=Bayonet Neill-Concelman connector,
    description={is a widely used small coaxial RF connector with a quick bayonet connection designed for up to a few GHz. A \qty{50}{\ohm} and a \qty{75}{\ohm} variant exist. It is used on radio systems, oscilloscopes, test equipment and video hardware}
}
\newglossaryentry{SMAlbl}{
    name=SubMiniature version A connector,
    description={is a common small coaxial RF connector with a screw-on connection designed for high frequencies (tens of GHz) often used for WiFi antennas and handheld radio devices among others}
}
\newglossaryentry{python}{
    name=Python,
    description={is a high-level interpreted general-purpose cross-platform programming language designed by Guido van Rossum. It focuses on readability and ease of use with a \enquote{batteries included} approach. The \href{https://peps.python.org/pep-0020/}{Zen of Python} states among others: \enquote{There should be one -- and preferably only one -- obvious way to do it}. (For the seasoned \enquote{Pythoneer}: Try \enquote{\lstinline[language=Python]{import this}} and \enquote{\lstinline[language=Python]{import antigravity}})}
}
\newglossaryentry{RPlbl}{
    name=RedPitaya,
    description={is a company producing credit card sized computers including an \acrshort{fpga} which run open-source software (the hardware itself is \emph{not} open-source). In the context of the thesis, this refers to the specific board used -- a RedPitaya \href{https://redpitaya.com/sdrlab-122-16/}{SDRlab 122-16} based on a Xilinx \acrshort{soc} (Zynq 7020 with Dual ARM Cortex A9, \qty{122.88}{\mega\hertz} clock and \qty{50}{\ohm} terminated \acrshort{rf} inputs)}
}
\newglossaryentry{GNUlbl}{
    name=GNU,
    description={is an extensive collection of \gls{fs} developed within the GNU Project which can be used to form a complete operating system -- the most famous one known as Linux. Its goal is to give computer users freedom and control in their use of computers by developing software under the copyleft \acrshort{gpl}, that guarantees access to the source code of the software}
}
\newglossaryentry{fs}{
    name=Free Software,
    description={is software available with a license that allows everyone to not only run but also look at, change and redistribute it freely -- i.e. it is distributed with the source code. It is thus different from freeware and especially proprietary software}. The FSF puts it as: \enquote{Think of \enquote{free} as in \enquote{free speech} not as in \enquote{free beer}.}
}
\newglossaryentry{lcrmeter}{
    name=LCR meter,
    description={is an electronic test equipment to measure inductance (L), capacitance (C) and resistance (R)}
}
\newglossaryentry{kicad}{
    name=KiCAD,
    description={is an open source \gls{fs} schematic capture and electronic design software endorsed by CERN for open hardware development}
}

% Glossary entries (used in text with e.g. \acrfull{fpsLabel} or \acrshort{fpsLabel})
\newacronym[longplural={Frames per Second}]{fpsLabel}{FPS}{Frame per Second}
\newacronym[longplural={Tables of Contents}]{tocLabel}{TOC}{Table of Contents}

\newacronym{mr}{MR}{\gls{MRlbl}}
\newacronym{nmr}{NMR}{\gls{NMRlbl}}
\newacronym{ftnmr}{FT-NMR}{\gls{FT-NMRlbl}}
\newacronym{cwnmr}{CW-NMR}{\gls{CW-NMRlbl}}
\newacronym{sma}{SMA}{\gls{SMAlbl}}
\newacronym{bnc}{BNC}{\gls{BNClbl}}
\newacronym{rf}{RF}{radio frequency}
\newacronym{tx}{TX}{transmit}
\newacronym{rx}{RX}{receive}
\newacronym{lna}{LNA}{low-noise amplifier}
\newacronym{rp}{RP}{\gls{RPlbl}}
\newacronym{fpga}{FPGA}{Field-Programmable Gate Array}
\newacronym{soc}{SoC}{System on a Chip}
\newacronym{pa}{PA}{power amplifier}
\newacronym{fid}{FID}{Free Induction Decay}
\newacronym{linux}{Linux}{\gls{GNUlbl}/Linux}
\newacronym{gnu}{GNU}{\gls{GNUlbl}'s Not Unix!}
\newacronym{gpl}{GPL}{\gls{GNUlbl} General Public License}
\newacronym{ip}{IP}{Internet Protocol}
\newacronym{fft}{FFT}{Fast Fourier Transform}
\newacronym{dhcp}{DHCP}{Dynamic Host Configuration Protocol}
\newacronym{ssh}{SSH}{Secure Shell}
\newacronym{pep}{PEP}{Python Enhancement Proposal}
\newacronym{pip}{pip}{pip Install Packages}
\newacronym{mri}{MRI}{Magnetic Resonance Imaging}
\newacronym{mmic}{MMIC}{Monolithic Microwave Integrated Circuit}
\newacronym{dma}{DMA}{Direct Memory Access}
\newacronym{tr}{T/R}{Transmit/Receive}
\newacronym{pcb}{PCB}{Printed Circuit Board}
\newacronym{marcos}{MaRCoS}{MAgnetic Resonance COntrol System}
\newacronym{cic}{CIC}{Cascaded Integrator-Comb}
\newacronym{spdt}{SPDT}{Single Pole, Double Throw}
\newacronym{spi}{SPI}{Serial Peripheral Interface}
\newacronym{adc}{ADC}{Analogue-to-ditigal converter}
\newacronym{opamp}{OpAmp}{Operational Amplifier}
\newacronym{vna}{VNA}{Vector Network Analyser}
\newacronym{dc}{DC}{direct current}
\newacronym{sdr}{SDR}{Software Defined Radio}
\newacronym{mpn}{MPN}{Manufacturer Part Number}
\newacronym{api}{API}{Application Programming Interface}
\newacronym{bom}{BOM}{Bill Of Material}
\newacronym{snr}{SNR}{Signal-to-Noise Ratio}
\newacronym{iid}{IID}{Independent and Identically Distributed}
\newacronym{gwn}{GWN}{Gaussian White Noise}
\newacronym{clt}{CLT}{Central Limit Theorem}
\newacronym{std}{STD}{Standard Deviation}
\newacronym{rms}{RMS}{Root Mean Square}
\newacronym{tms}{TMS}{Tetramethylsilane}
\newacronym{fet}{FET}{Field-Effect Transistor}
\newacronym{ac}{AC}{Alternating Current}
\newacronym{gpio}{GPIO}{General-Purpose Input/Output}
\newacronym{cli}{CLI}{Command-Line Interface}
\newacronym{vat}{VAT}{Value Added Tax}
\newacronym{chf}{CHF}{Swiss Francs}
\newacronym{dac}{DAC}{Digital-to-analog converter}
\newacronym{led}{LED}{Light Emitting Diode}
\newacronym{ic}{IC}{Integrated Circuit}
\newacronym{usb}{USB}{Universal Serial Bus}

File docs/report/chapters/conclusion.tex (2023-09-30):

\setchapterpreamble[u]{
    \margintoc\hfil%
    % \dictum[English Proverb]{Hindsight is 20/20}
    \dictum[Bill Gates]{I choose a lazy person to do a hard job. Because a lazy person will find an easy way to do it.}
}
\chapter{Conclusion}
\labch{conclusion}
% Higher level discussion/results by referencing back to motivation
% Provide an outlook on further work, e.g. by referencing back to unfinished/unacomplished goals in the motivation

\refch{concepts} briefly introduced the basic concepts needed to understand the electronics and chemistry of the spectrometer. \refch{methods} then looked at the different parts of it in detail, whereas \refch{complete} described the usage of the whole system. Finally, \refch{results} described and discussed the experimental results obtained with the designed system.

An affordable low-field low-cost easy-to-use and easy-to-build NMR spectrometer was designed, built characterised and tested.

Immediate next steps include the completion of the shimming system and more iterations on the probe. Tuning and matching should be possible from outside the magnet for easier and quicker operation in addition to shielding to remove the RF noise. The improvement points mentioned at the end of each sections should be addressed.

The main functions separated into individual parts allow for easy reconfiguration and experimentation during the early stages of the project. A final design could later integrate them on a single \acrshort{pcb}, reducing cost further as well as noise due to a shorter path and raising signal power due to fewer reflections and impedance mismatches.

Looking especially towards its application in the Global South, the temperature behaviour and stability of the system need first to be characterized and then possibly compensated through isolation cooling and/or heating.

With the recently increasing focus on low-field low-cost magnetic resonance work leveraging the higher capabilities and lower costs of modern electronics --- especially in the \acrshort{sdr} domain --- a joint effort and interface would be highly advantageous as well. Some homebrew NMR console control software solutions exist and have been mentioned before. A lot of them are rudimentary and not compatible with each other. While software solutions for analysing spectra exist, processing spectra can be cumbersome not only due to the various file formats but also due to the focus of existing tools on commercial systems which often provide proprietary processing options.

There is still a lot to be done before \magnethical{} is ready for deployment. It lays the groundwork for further optimization, integration and exploration. It is the beginning of a great new quest!

% Significant work remains before \magnethical{} can be deemed complete. The current stage of development serves as a foundational step toward subsequent optimization, seamless integration, and comprehensive exploration. This juncture signifies the commencement of an ambitious and promising journey ahead.

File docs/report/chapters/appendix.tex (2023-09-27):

\chapter{Schematics}
\labch{schematics}
\section{The power amplifier}
\labsec{poweramp-schematic}


\section{The switch}
\labsec{switch-schematic}


\section{The low noise amplifier}
\labsec{lna-schematic}


\section{The 32-channel current source}
\labsec{32-channel-current-source-schematic}






\section{The magnet}
\labsec{magnet-schematic}


\chapter{Lists of Parts}
\labch{lists-of-parts}
% TODO: Maybe add prices for all individual parts
Below are the complete part lists for the schematics above --- also called \acrshort{bom}s. A lot of standard parts are available from many different manufacturers, the given \acrfull{mpn} in these cases are only one of many possible options. For example most of the RLC parts, the linear power supplies (7850, LM317, \ldots) and the pin headers --- among others.

As customary in a lot of designs, the comma dot has often been replaced by the SI-Prefix for the given value or the variable name in case of no prefix. For example, 4k7 for a resistor is equivalent to \qty{4.7}{\kilo\ohm}. Equivalently, a 5u6 capacitor has a value of \qty{5.6}{\micro\farad}. If there is no prefix, the symbol is sometimes used, for example, 37R4 is equal to a \qty{37.4}{\ohm} resistor. This is usually done for better readability and less ambiguity --- especially on bad prints where the point can easily vanish.

\newpage
\section{The power amplifier}
\labsec{poweramp-parts}
\begin{center}
    \begin{tabular}{@{} llll @{}}
        \toprule
        Qty & Reference(s)              & Value                       & \acrshort{mpn}     \\
        \midrule
        6   & C1, C2, C3, C4, C10, C15  & 100n,50V,10\%               & C0805C104J5RACTU   \\
        6   & C5, C11, C8, C9, C13, C14 & 1u,50V,10\%                 & CL21B105KBFNNNG    \\
        2   & C6, C12                   & 1n,50V,10\%                 & 08055C102KAT2A     \\
        1   & C7                        & 68p,50V                     & 08055A680JAT2A     \\
        2   & C16, C17                  & 10u,50V,10\%                & GRM21BR61H106KE43L \\
        2   & C18, C19                  & 130p/50V                    & GRM2165C1H131JA01D \\
        1   & D1                        & SS13HE,Schottky,30V,1A      & SS13HE             \\
        4   & D2, D3, D4, D5            & S1B (1N4002)                & S1B-13-F           \\
        1   & F2                        & PTC fuse,6V,0.75A,0.2s,40mΩ & 0805L075SL         \\
        1   & J1                        & Power                       & 68491-102HLF       \\
        1   & J2                        & RF\_IN                      & 142-0701-851       \\
        1   & J3                        & RF\_OUT                     & 142-0701-851       \\
        1   & J4                        & Power\_Enable               & 68491-102HLF       \\
        1   & L1                        & 5u6                         & CC453232-5R6KL     \\
        1   & L2                        & 470n                        & L-15FR47JV4E       \\
        1   & L3                        & 360n,5\%,RF                 & 36502AR36JTDG      \\
        1   & Q1                        & MMBT3904                    & MMBT3904-7-F       \\
        1   & Q2                        & BCP51                       & BCP51,115          \\
        2   & R1, R2                    & 150                         & AC0805FR-07150RL   \\
        1   & R3                        & 37R4                        & CR0805-FX-37R4ELF  \\
        2   & R4, R7                    & 240, 1\%                    & RC0805FR-07240RL   \\
        1   & R5                        & 715, 1\%                    & RT0805FRE07715RL   \\
        1   & R6                        & 2k43, 1\%                   & ERJ-6ENF2431V      \\
        2   & R8, R10                   & 1k                          & 1623131-1          \\
        1   & R9                        & 10k                         & CRCW080510K0FKEAC  \\
        1   & R11                       & 4k7                         & AC0805FR-074K7L    \\
        1   & U1                        & ADL5536                     & ADL5536ARKZ-R7     \\
        1   & U2                        & PHA-202+                    & PHA-202+           \\
        2   & U3, U4                    & LM317\_SOT-223              & LM317MQDCYR        \\
        \bottomrule
    \end{tabular}
\end{center}

\newpage
\section{The switch}
\labsec{switch-parts}
\begin{center}
    \begin{tabular}{@{} llll @{}}
        \toprule
        Qty & Reference(s) & Value                      & \acrshort{mpn}   \\
        \midrule
        3   & C1, C2, C3   & 1u/50V                     & CL21B105KBFNNNG  \\
        2   & C4, C5       & 200p/50V                   & C0805C201K5HACTU \\
        1   & C8           & 100n/50V                   & C0805C104J5RACTU \\
        1   & D1           & BAS321Z                    & BAS321Z          \\
        1   & J1           & RF1                        & 142-0701-851     \\
        1   & J2           & RF2                        & 142-0701-851     \\
        1   & J3           & RFC                        & 142-0701-851     \\
        1   & J4           & 2x,2.54mm pitch,pin header & 68491-102HLF     \\
        1   & J5           & 4x,2.54mm pitch,pin header & 69190-104HLF     \\
        1   & U1           & 7805                       & UA78M05IDCYR     \\
        1   & U2           & QPC6324                    & QPC6324          \\
        \bottomrule
    \end{tabular}
\end{center}

\newpage
\section{The low noise amplifier}
\labsec{lna-parts}
\begin{center}
    \begin{tabular}[c]{@{} llll @{}}
        \toprule
        Qty & Reference(s) & Value          & \acrshort{mpn}    \\
        \midrule
        1   & C1           & 1p5,50V,10\%   & CC0805BRNPO9BN1R5 \\
        2   & C2, C4       & 2u2,25V,10\%   & CL21A225KAFNNNG   \\
        2   & C3, C7       & 100n,50V,10\%  & CL21B104KBCNNNC   \\
        1   & C5           & 1n,50V,10\%    & CL21B102KBANFNC   \\
        1   & C6           & 10u,25V,10\%   & CL21A106KAYNNNG   \\
        2   & C8, C9       & 1u,50V,10\%    & CL21B105KBFNNNG   \\
        1   & D1           & BAV99          & BAV99             \\
        1   & D2           & BAS321Z        & BAS321Z           \\
        1   & J1           & RF\_IN         & 142-0701-851      \\
        1   & J2           & RF\_OUT        & 142-0701-851      \\
        1   & J3           & Power          & 68491-102HLF      \\
        1   & L1           & 15u            & CV201210-150K     \\
        1   & L2           & 5n1,5\%,Unshld & 0805HT-5N1TJLC    \\
        1   & R1           & 1k5,1\%        & RT0805FRE101K5L   \\
        1   & U1           & PHA-13LN       & PHA-13LN+         \\
        1   & U2           & 7805           & UA78M05IDCYR      \\
        \bottomrule
    \end{tabular}
\end{center}

\newpage
\section{The 32-channel current source}
\labsec{power-parts}
\begin{longtable}[c]{@{} lp{5cm}p{5cm}l @{}}
    \toprule
    Qty & Reference(s)                                                                                                                                                                                                                                                                                                                                                             & Value                                               & \acrshort{mpn}  \\
    \midrule
    40  & C1, C3, C9, C10, C15, C16, C21, C22, C27, C28, C29, C31, C37, C38, C43, C44, C49, C50, C55, C56, C57, C59, C65, C66, C71, C72, C77, C78, C83, C84, C85, C87, C93, C94, C99, C100, C105, C106, C111, C112                                                                                                                                                                 & 10u, tantalum                                       & TMCP1A106KTRF   \\
    72  & C2, C4, C5, C6, C7, C8, C11, C12, C13, C14, C17, C18, C19, C20, C23, C24, C25, C26, C30, C32, C33, C34, C35, C36, C39, C40, C41, C42, C45, C46, C47, C48, C51, C52, C53, C54, C58, C60, C61, C62, C63, C64, C67, C68, C69, C70, C73, C74, C75, C76, C79, C80, C81, C82, C86, C88, C89, C90, C91, C92, C95, C96, C97, C98, C101, C102, C103, C104, C107, C108, C109, C110 & 100n, ceramic, low ESR, low ESI                     & 0805ZD104KAT2A  \\
    2   & J1, J3                                                                                                                                                                                                                                                                                                                                                                   & Red, banana power plug, enclosure                   & 6091            \\
    1   & J2                                                                                                                                                                                                                                                                                                                                                                       & Black, banana power plug, enclosure                 & 6092            \\
    1   & J4                                                                                                                                                                                                                                                                                                                                                                       & 10pos, 2row, DIN41651, 2.54mm pitch, idc            & 72454-010LF     \\
    4   & J5, J6, J7, J8                                                                                                                                                                                                                                                                                                                                                           & 16pos, 2row, DIN41651, 2.54mm pitch, idc            & 72454-016LF     \\
    1   & N1                                                                                                                                                                                                                                                                                                                                                                       & Enclosure, Hammond 1590                             & 1590Z150        \\
    32  & R1, R3, R11, R13, R21, R23, R31, R33, R41, R43, R51, R53, R61, R63, R71, R73, R81, R83, R91, R93, R101, R103, R111, R113, R121, R123, R131, R133, R141, R143, R151, R153                                                                                                                                                                                                 & 10k                                                 & RT0805FRE1310KL \\
    64  & R2, R4, R7, R8, R12, R14, R17, R18, R22, R24, R27, R28, R32, R34, R37, R38, R42, R44, R47, R48, R52, R54, R57, R58, R62, R64, R67, R68, R72, R74, R77, R78, R82, R84, R87, R88, R92, R94, R97, R98, R102, R104, R107, R108, R112, R114, R117, R118, R122, R124, R127, R128, R132, R134, R137, R138, R142, R144, R147, R148, R152, R154, R157, R158                       & 2k                                                  & RT0805FRE072KL  \\
    32  & R5, R6, R15, R16, R25, R26, R35, R36, R45, R46, R55, R56, R65, R66, R75, R76, R85, R86, R95, R96, R105, R106, R115, R116, R125, R126, R135, R136, R145, R146, R155, R156                                                                                                                                                                                                 & 1k                                                  & RT0805FRE071KL  \\
    32  & R9, R10, R19, R20, R29, R30, R39, R40, R49, R50, R59, R60, R69, R70, R79, R80, R89, R90, R99, R100, R109, R110, R119, R120, R129, R130, R139, R140, R149, R150, R159, R160                                                                                                                                                                                               & 1, precision, current sense                         & ERJ-6DQF1R0V    \\
    4   & U1, U10, U19, U28                                                                                                                                                                                                                                                                                                                                                        & AD5676R                                             & AD5676RBRUZ     \\
    16  & U2, U4, U6, U8, U11, U13, U15, U17, U20, U22, U24, U26, U29, U31, U33, U35                                                                                                                                                                                                                                                                                               & LMV358                                              & LMV358IDR       \\
    16  & U3, U5, U7, U9, U12, U14, U16, U18, U21, U23, U25, U27, U30, U32, U34, U36                                                                                                                                                                                                                                                                                               & NCV0372                                             & NCV0372BDWR2G   \\
    \midrule
    1   & -                                                                                                                                                                                                                                                                                                                                                                        & 10pos, 2row, DIN41651, 2.54mm pitch, ids, enclosure & 4610-6000       \\
    4   & -                                                                                                                                                                                                                                                                                                                                                                        & 16pos, 2row, DIN41651, 2.54mm pitch, idc, enclosure & 4616-6000       \\
    1   & -                                                                                                                                                                                                                                                                                                                                                                        & 10pos, 2row, DIN41651, 2.54mm pitch, ids, cable     & 71600-310LF     \\
    4   & -                                                                                                                                                                                                                                                                                                                                                                        & 16pos, 2row, DIN41651, 2.54mm pitch, idc, cable     & 71600-316LF     \\
    \bottomrule
\end{longtable}

% \chapter{About this thesis}
% \labch{about}

% This thesis was heavily influenced by Jean-Luc Doumont's \enquote{English Communication for Scientists} \sidecite{doumontEnglishCommunicationScientists2010}.

% \chapter{Schematics}

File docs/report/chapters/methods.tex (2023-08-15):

\chapter{Methods}
\label{ch:methods}
% Write in theorem-proof fashion

building the coil
building the power supply

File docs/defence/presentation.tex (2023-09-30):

\documentclass{ethpresentation}
\usepackage{multimedia}
% \setbeameroption{show notes on second screen} % use e.g. pympress to view

% Simple handout with just the slides
% "article" mode is better, but this might be useful in a pinch?
% \documentclass[handout]{ethpresentation}
% \usepackage{pgfpages}
% \pgfpagesuselayout{6 on 1}[a4paper,border shrink=5mm]

% Footnotes for sources without number
\let\svthefootnote\thefootnote
\NewDocumentCommand{\freefootnote}{m}{
  \let\thefootnote\relax%
  \footnotetext{#1}%
  \let\thefootnote\svthefootnote%
}

% Regular footnotes use letters
\renewcommand*{\thefootnote}{\fnsymbol{footnote}}

% Logo
\NewDocumentCommand{\magnethical}{}{\textnormal{\textsl{\textmd{\textsl{magn\textbf{ETH}ical}}}}}

% Notes:
% - Include challenges faced and overcome, so it's mentioned
% - Include lessons learned
% - estimate 2min per slide on average 
%  -> was a bit faster (~43min for 29 slides), took ~60min including demonstration

%%%%%%%%%%%%%%%%%%%%%%%%%%%%%%%%%%%%%%%%%%%%%%%%%%%%%%%%%%%%%%%%%%%%%%%%%%%%%%%
% Metadata
%%%%%%%%%%%%%%%%%%%%%%%%%%%%%%%%%%%%%%%%%%%%%%%%%%%%%%%%%%%%%%%%%%%%%%%%%%%%%%%

\title{\Huge\magnethical}
\subtitle{Master Thesis: Building a 25\,MHz NMR Spectrometer}
\date{\today}
\author{Maximilian Stabel}
\institute{ETH Zürich}

%%%%%%%%%%%%%%%%%%%%%%%%%%%%%%%%%%%%%%%%%%%%%%%%%%%%%%%%%%%%%%%%%%%%%%%%%%%%%%%
% Content
%%%%%%%%%%%%%%%%%%%%%%%%%%%%%%%%%%%%%%%%%%%%%%%%%%%%%%%%%%%%%%%%%%%%%%%%%%%%%%%

\begin{document}
\maketitle % show when people are walking in

% Attention Getter
\begin{frame}
    \centering
    \emph{\enquote{What I cannot create, I do not understand}}

    \vspace{\baselineskip}

    \hfill{}---Richard Feynman
    \note[item]{In the spirit of Richard Feynman... }
    \note[item]{My master thesis is about building an NMR spectrometer}
    \note[item]{I'm Max and I'll be your host for today}
    \note[item]{Speaking of understanding...}
\end{frame}

% Need / Motivation
\begin{frame}{There is not a lot of NMR research in the Global South}
    \centering
    

    \(\frac{\text{NMR publications}}{\text{million people}}\)
    \note[item]{Only publications, does not include use of NMR!}
    \note[item]{I'm Max and I'll talk about my master thesis: building a 25MHz NMR spectrometer}
\end{frame}
\note{Reminder: What is NMR spectrometer}

\begin{frame}{Nuclear Magnetic Resonance}
    \begin{itemize}
        \item Nuclei absorb radio waves at a certain frequency when inside a magnetic field
        \item The nuclei emit radio waves at that same frequency when excited this way
        \item \(f \sim{} B_0\) and surroundings
    \end{itemize}
\end{frame}

\note{
    \begin{itemize}
        \item You: Understanding for own experiments
        \item The better we know the better we can use
        \item Push NMR development --- better machines
        \item Transition: if not about you personally --- more globally: applications
    \end{itemize}
}

\begin{frame}{NMR is used across various fields}
    \note[item]{Some of you already know, but here are some reasons why NMR is useful}
    \begin{itemize}
        \item Research (Structure Analysis, Drug Discovery, \ldots)
        \item Medicine (Imaging, Diagnosis, \ldots)
        \item Industry (Process Control, Drug screening, \dots)
        \item Education (Quantum Mechanics, Quantum Computing, \ldots)
    \end{itemize}
\end{frame}

% Task / Main Message
% One sentence to remember if they remember only one
\begin{frame}[standout]
    \centering
    Build an accessible\\NMR spectrometer
    \note[item]{The goal of my thesis was...}
\end{frame}

% Preview
% Give short overview of main points to come
% DONT just list ("I will talk about ..., then about ...)
% Integrate with main message, include audience ("we")
% Introduction to NMR
% Will talk about the parts of the spectrometer
% Do a short demonstration..
% Show table of contents, without anything above (introduction, ...) and without conclusion/review/close
\begin{frame}{Preview}
    \tableofcontents
\end{frame}

% Main Body
% Remember to do transitions!
\section{The parts}
\begin{frame}{Our goal is to build an accessible NMR spectrometer}
    \centering
    
    % \begin{circuitikz}
    %   \ctikzset{bipoles/amp/width=0.9}
    %   \draw[nodes={align=center}]
    %   (0,0) coordinate(mid)

    %   % RP
    %   (mid) node[draw, minimum height=5.5cm, minimum width=2.5cm,label=Console](redpitaya){}
    %   (redpitaya.west) coordinate(inp) node[right]{Input}
    %   ($(redpitaya.east)!0.75!(redpitaya.north east)$) coordinate(rptx) node[left]{Transmit}
    %   ($(redpitaya.east)!0.75!(redpitaya.south east)$) coordinate(rprx) node[left]{Receive}

    %   % Computer
    %   (-3,0) node(seq){Sequence}
    %   (seq.east) -- (redpitaya.west) node[inputarrow]{} coordinate(console)

    %   % TX
    %   (rptx) to[lowpass,l=Lowpass,>] ++(3,0)
    %   to[amp,l=Amplifier,>] ++(3,0) coordinate(tx)

    %   % Circulator
    %   (mid -| tx) node[circulator,label={left:Switch}](circ){}
    %   (tx) -| (circ.n) node[inputarrow,rotate=270]{}

    %   % RX
    %   (rprx -| circ) coordinate(rx)
    %   (circ.s) |- (rx)
    %   (rx) to[amp,l=Amplifier,>] ++(-3,0)
    %   to[lowpass,l=Lowpass,>] ++(-3,0) node[inputarrow,rotate=180]{}

    %   % Probe
    %   (circ.e) -- ++(1,0)
    %   node[dinantenna](probe){}
    %   node[below=1ex]{Coil}
    %   ;
    % \end{circuitikz}
    \note[item]{Go through the parts left to right}
    \note[item]{Our switch only, others might include more analog processing}
\end{frame}

\begin{frame}{The console\\is a ready-made FPGA board\footnote{Red Pitaya SDRlab 122-16}}
    % \centering
    \vspace*{-1\baselineskip}
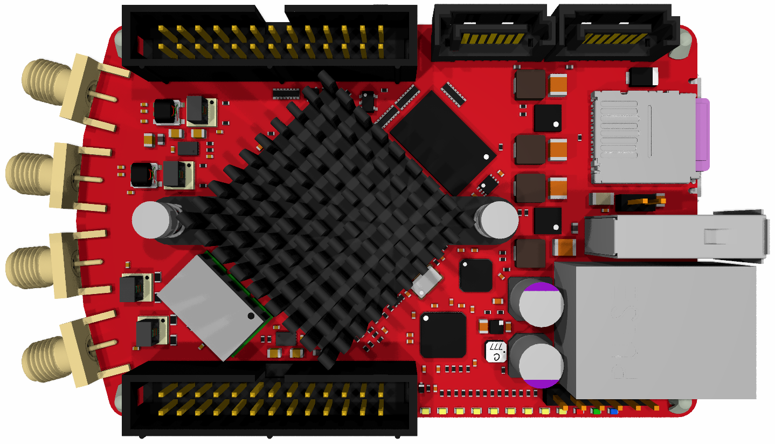
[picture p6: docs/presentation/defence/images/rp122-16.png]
    
    \begin{tikzpicture}[overlay, remember picture]
        \node[anchor=north east, inner sep=0] (block) at (current page.north east) {\colorbox{white}{}};
        \draw[red, ultra thick, rounded corners] (block.south west) ++(0.1,0.2) rectangle ++(2.5,3);
    \end{tikzpicture}
    \note[item]{FPGA == programmable hardware, very fast}
    \note[item]{oversampling}
    \note[item]{CIC filter (decimation, low pass filter, moving average)}
    \note[item]{The signal needs to be filtered and then amplified: Next Slide}
\end{frame}

\begin{frame}{The power amplifier has two stages}
    \centering
    \vspace*{4\baselineskip}
    \begin{columns}
        \begin{column}{0.2\textwidth}
            \vspace*{2\baselineskip}
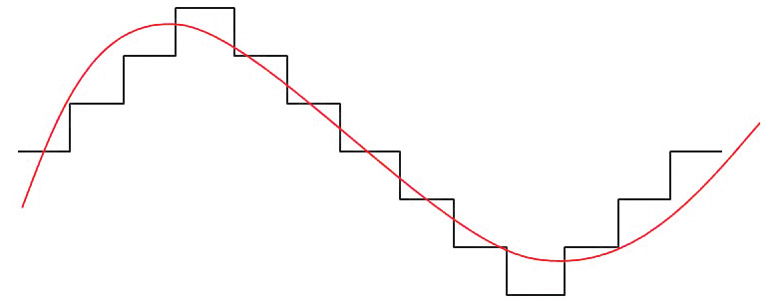
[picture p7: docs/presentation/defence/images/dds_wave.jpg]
            
        \end{column}
        \begin{column}{0.8\textwidth}
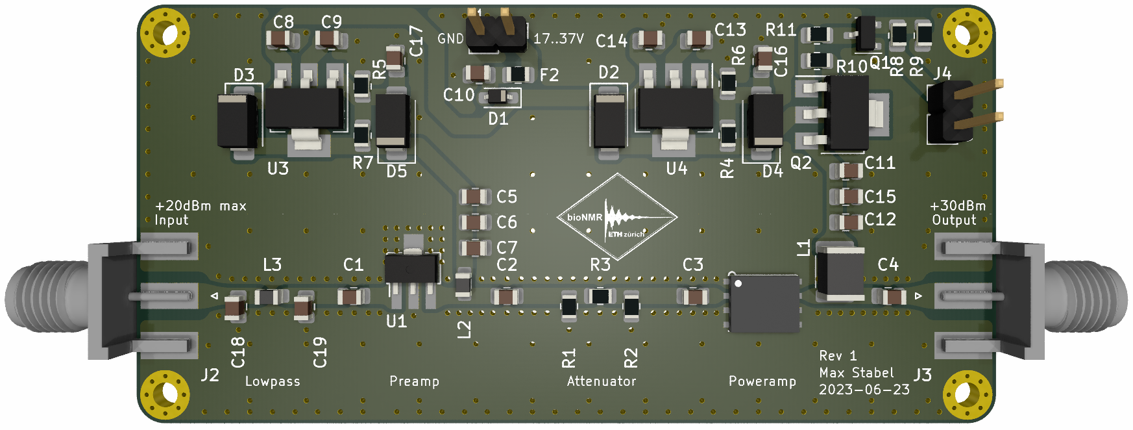
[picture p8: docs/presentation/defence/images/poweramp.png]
            
        \end{column}
    \end{columns}
    \begin{tikzpicture}[overlay, remember picture]
        \node[anchor=north east, inner sep=0] (block) at (current page.north east) {\colorbox{white}{}};
        \draw[red, ultra thick, rounded corners] (block.south west) ++(2.7,2.2) rectangle ++(2.3,1);
    \end{tikzpicture}
    % \includegraphics[width=0.9\textwidth]{poweramp.png}
    \note[item]{We want cheap, so using a simple is the obvious first approach}
    \note[item]{Unfortunately there's a lot to do:%
        \begin{itemize}
            \item Input/Output Impedance Matching
            \item Bias Tee
            \item DC coupling
            \item stability calculations
            \item feedback
            \item temperature compensation (current feedback)
        \end{itemize}
    }
    \note[item]{A complete amplifier is quite expensive}
    \note[item]{Solution: Use monolithic (integrated) amplifier}
    \note[item]{Take care of heat dissipation (Class-A)}
    \note[item]{dB is logarithmic unit}
\end{frame}

\begin{frame}{The low-noise amplifier had\\instability issues}
    \centering
    \vspace*{2\baselineskip}
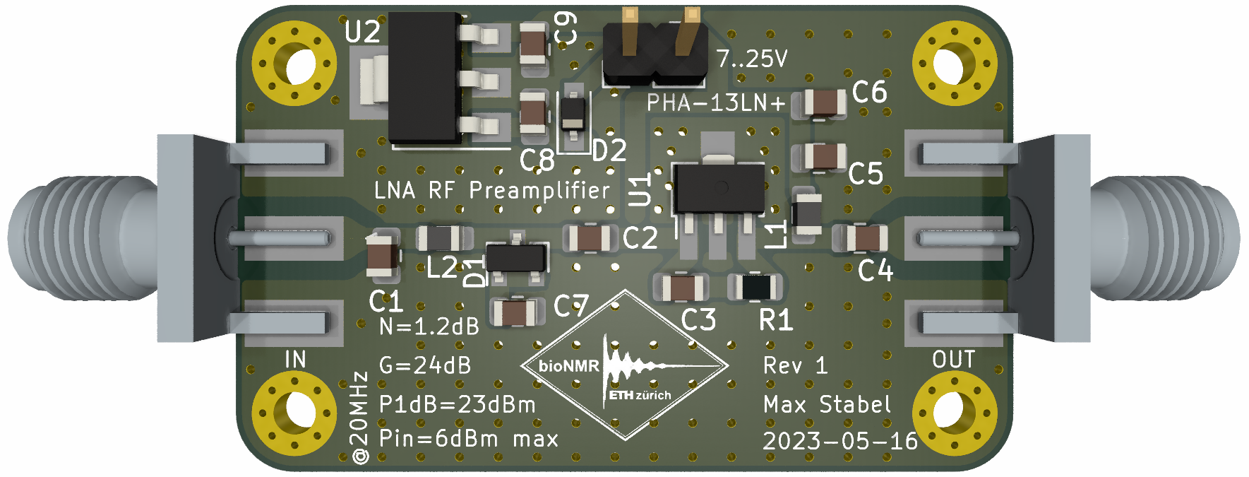
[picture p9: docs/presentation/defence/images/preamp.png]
    
    \begin{tikzpicture}[overlay, remember picture]
        \node[anchor=north east, inner sep=0] (block) at (current page.north east) {\colorbox{white}{}};
        \draw[red, ultra thick, rounded corners] (block.south west) ++(4,0.1) rectangle ++(1,1);
    \end{tikzpicture}
    \note[item]{Low-noise }
    \note[item]{Feedback loop --- stray capacitance}
    \note[item]{Solution: Smaller housing, shorter loop}
    \note[item]{We need 3x for enough gain}
\end{frame}

\begin{frame}{We use a transistor-based active switch}
    \centering
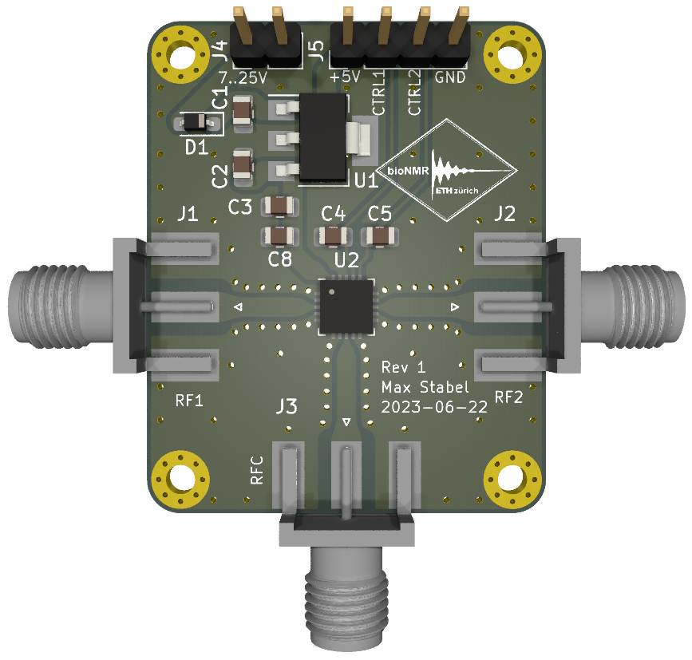
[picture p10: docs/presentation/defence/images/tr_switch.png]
     \hspace*{5em}
    \begin{tikzpicture}[overlay, remember picture]
        \node[anchor=north east, inner sep=0] (block) at (current page.north east) {\colorbox{white}{}};
        \draw[red, ultra thick, rounded corners] (block.south west) ++(4.3,1.25) rectangle ++(1.3,0.8);
    \end{tikzpicture}
    \note[item]{Active}
    \note[item]{Isolation: \qty{60}{dB}}
    \note[item]{Silicon-on-insulator (not pHEMT GaAs) i.e. FET tech, not PIN-Diode}
    \note[item]{PIN-Diode switch also possible, but
        \begin{itemize}
            \item usually higher leakage
            \item slower switching
            \item harder to integrate on a chip
            \item but higher power capabilities
        \end{itemize}
    }
\end{frame}

\begin{frame}{The probe}
    % \centering
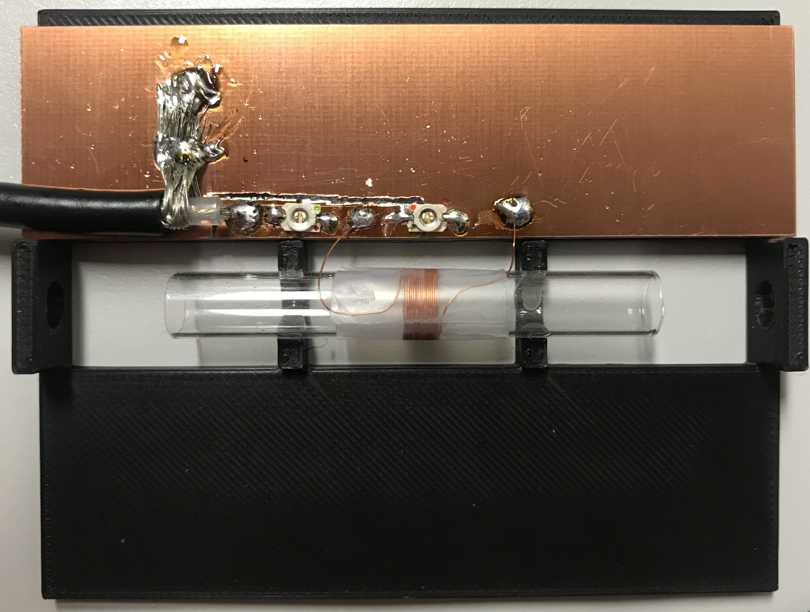
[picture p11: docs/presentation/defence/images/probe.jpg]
    
    \begin{tikzpicture}[overlay, remember picture]
        \node[anchor=north east, inner sep=0] (block) at (current page.north east) {\colorbox{white}{}};
        \draw[red, ultra thick, rounded corners] (block.south west) ++(5.6,1.25) rectangle ++(0.6,1);
    \end{tikzpicture}
    \note[item]{Many turns --- high inductance --- low capacitance --- sensitive to stray capacitance}
\end{frame}

\begin{frame}{A 32-channel current supply is designed but untested}
    \centering
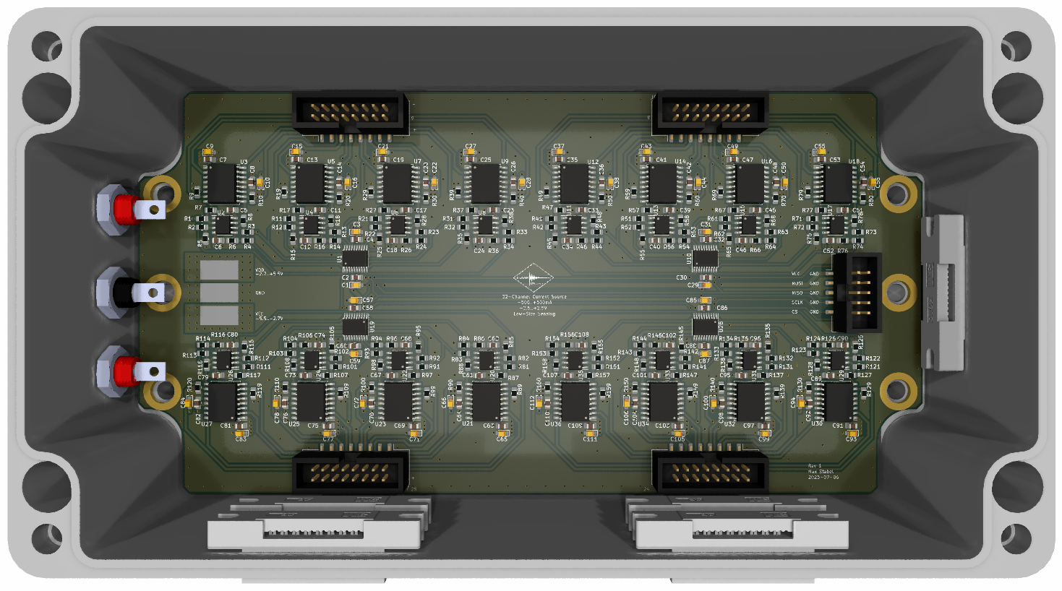
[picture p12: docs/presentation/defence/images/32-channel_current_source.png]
    
\end{frame}

\section{The complete setup}

\begin{frame}{Our NMR is affordable \ldots}
    \vspace*{-0.5\baselineskip}
    \begin{table}
        \begin{tabular}{@{}
                l
                S[table-format=7.0,table-align-text-pre=false]
                S[table-format=3.2,table-align-text-pre=false]
                S[table-format=5.2,table-align-text-pre=false]
                @{}}
            \toprule
                                & {\qty{600}{\mega\hertz}\footnote{estimated costs}} & {mini-circuits} & {\magnethical}          \\
            \midrule
            Power Amplifier     & 50000                                              & 323.49          & 36.01                   \\
            Switch              & {-}                                                & 82.06           & 20.05                   \\
            Probe               & 100000                                             & {-}             & {\approx} 15.00         \\
            Low-Noise Amplifier & 50000                                              & 409.38          & 73.11                   \\
            Shim Driver         & {-}                                                & {-}             & 257.08                  \\
            Console             & 200000                                             & {-}             & 662.53                  \\
            Magnet              & 1000000                                            & {-}             & {\approx} 9000.00       \\
            \bottomrule
            \textbf{Sum}        &                                                    &                 & \textbf{\num{10142.80}} \\
        \end{tabular}
    \end{table}
    \freefootnote{Prices incl. VAT [CHF]}
\end{frame}

\begin{frame}{\ldots{} competitive \ldots{}}
    \begin{table}
        \begin{tabular}{@{} lrrr @{}}
            \toprule
                                           & Superconducting                        & Benchtop                            & \magnethical{}                                             \\
            \midrule
            Price [k\,CHF]                 & \numrange[range-phrase=--]{200}{18000} & \numrange[range-phrase=--]{50}{150} & \approx\num{10}                                            \\
            Frequency [\unit{\mega\hertz}] & \numrange[range-phrase=--]{300}{1200}  & \numrange[range-phrase=--]{40}{125} & \num{25}                                                   \\
            Resolution [\unit{\hertz}]     & \approx\num{0.2}                       & \numrange[range-phrase=--]{0.2}{1}  & \approx \num{2.5}/\num{50}\footnote[2]{with/without shims} \\
            Weight [\unit{\kilo\gram}]     & \numrange[range-phrase=--]{600}{15000} & \numrange[range-phrase=--]{25}{150} & \approx\num{5}                                             \\
            % \bottomrule
        \end{tabular}
    \end{table}
    \freefootnote{For 5mm standard NMR tubes}
\end{frame}

% Add picture of complete setup
\begin{frame}{\ldots{} and portable}
    \vspace*{-2\baselineskip}
    \centering
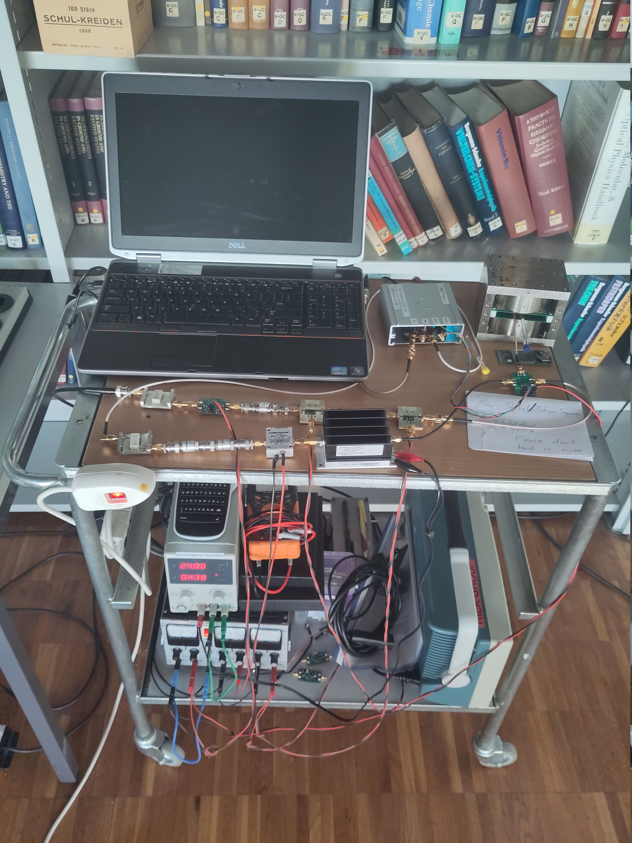
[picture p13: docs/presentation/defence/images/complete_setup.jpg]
    
\end{frame}

% Results
\section{Experimental Results}

\begin{frame}{Simple Pulse Sequence}
    \centering
    \includesvg[width=0.5\textwidth]{simple_pulse_sequence.svg}
\end{frame}

\begin{frame}{We can already see a water FID}
    \centering
    % \includegraphics[width=0.9\textwidth]{images/fid_sine_fit.pdf}
    % TODO: add T2*
    \begin{tikzpicture}
        \node[anchor=south west,inner sep=0] (image) at (0,0) {
            
        };
        \begin{scope}[overlay]
            \node[anchor=east](t2) at (image.north east){\(T_2^* = \qty{2.55}{\milli\second}\)};
        \end{scope}
    \end{tikzpicture}
    \note[item]{Outliers at the beginning are due to CIC filters}
\end{frame}

\begin{frame}{\ldots and do a Fourier transform}
    \centering
    \begin{tikzpicture}
        \node (fft)
        {
            
        };
        \begin{scope}[overlay]
            \node (structure) at (fft.north)
            [
                anchor=center,
                xshift=0.65cm,
                yshift=0cm
            ]
            {
                \includesvg[height=0.1\textheight]{images/h2o.svg}
            };
            \path[draw=grey,dashed,->] ([yshift=1mm,xshift=-3mm]structure.south east) to ([xshift=0.7cm,yshift=2.5cm]fft.center);
            \path[draw=grey,dashed,->] ([yshift=1mm,xshift=3mm]structure.south west) to ([xshift=0.6cm,yshift=2.5cm]fft.center);
            \node[anchor=north east](label) at (fft.north east){%
                \(
                \begin{aligned}
                    T_2^*       & = \qty{2.71}{\milli\second} \\
                    \text{FWHM} & = \qty{117.7}{\hertz}
                \end{aligned}
                \)
            };
        \end{scope}
    \end{tikzpicture}
    \note[item]{Not Lorentz because of missing shimming/inhomogeneities}
    \note[item]{Measured input signal of -92dBm/15.8uV resulted in amplitude of 2200}
    \note[item]{SNR of around 350, With FWHM 2.5Hz/1ppm we estimate snr of 11000}
\end{frame}

\begin{frame}{Toluene also has a visible signal}
    \centering
    
\end{frame}

\begin{frame}{We can even see the chemical shifts\\of the Toluene peaks!}
    \centering
    \begin{tikzpicture}
        \node (fft)
        {
            
        };
        \begin{scope}[overlay]
            \node (structure) at (fft.north)
            [
                anchor=north west,
                xshift=0mm,
                yshift=1.5cm
            ]
            {
                \includesvg[height=0.15\textheight]{images/toluene.svg}
            };
            \path[draw=grey,dashed,->] ([yshift=5mm,xshift=-4mm]structure.south east) to ([yshift=1.5cm,xshift=1.75cm]fft.center);
            \path[draw=grey,dashed,->] ([yshift=2mm,xshift=2mm]structure.south west) to ([yshift=3.1cm]fft.center);
        \end{scope}
    \end{tikzpicture}
    \note{It's a full tube of toluene, not a solution}
    \note[item]{Reasons for sidepeak: no apodization (truncation of FID), no shimming, inhomogeneities/not centred}
\end{frame}

\begin{frame}{Rabi nutation (pulse calibration) of water}
    \centering
    \begin{tikzpicture}
        \node (rabi)
        {
            
        };
        \begin{scope}[overlay]
            \node[anchor=north east](label) at (rabi.north east){%
                \(
                \begin{aligned}
                    2\pi{}          & \mathrel{\hat{=}} \qty{32.3}{\micro\second} \\
                    \frac{\pi{}}{2} & \mathrel{\hat{=}} \qty{8.07}{\micro\second}
                \end{aligned}
                \)
            };
        \end{scope}
    \end{tikzpicture}
    \note[item]{\(T_{period} = \qty{32}{\micro\second}\)}
    \note[item]{\(T_{\frac{\pi}{2}} = \qty{8}{\micro\second}\)}
\end{frame}

\begin{frame}{Spin Echo Sequence}
    \centering
    \includesvg[width=0.9\textwidth]{spin_echo_sequence.svg}
\end{frame}

\begin{frame}{Spin Echo Animation}
    \begin{center}
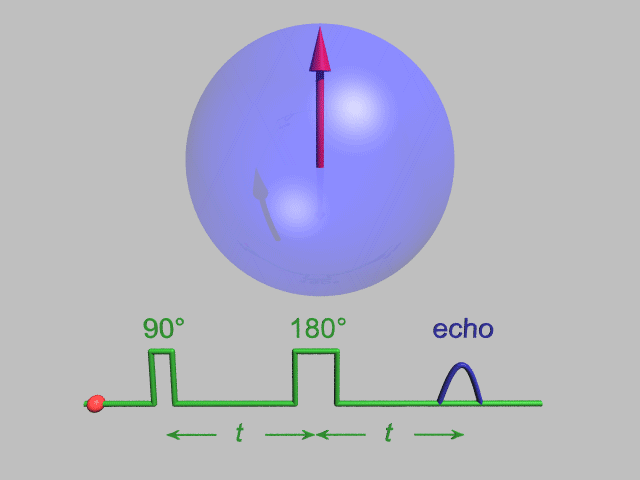
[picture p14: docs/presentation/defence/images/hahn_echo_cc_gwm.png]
        \movie[width=8.7cm,height=6.5cm]{}{./hahn_echo_cc_gwm.gif}
    \end{center}
    \freefootnote{\href{https://commons.wikimedia.org/wiki/File:GWM_HahnEcho.gif}{Gavin Morley --- CC BY-SA 3.0}}
\end{frame}

\begin{frame}{Spin Echo Measurement}
    \centering
    
\end{frame}

\begin{frame}{\(T_2\) decay of water}
    \centering
    \begin{tikzpicture}
        \node (decay)
        {
            
        };
        \begin{scope}[overlay]
            \node[anchor=north east](label) at (decay.north east){\(T_2 = \qty{190}{\milli\second}\)};
        \end{scope}
    \end{tikzpicture}
    \note[item]{\(T_2 = \)}  % Add to slide
\end{frame}

% Demonstration! Measure FID of water/toluene
% TODO: Backup slides with notebook screenshots of measurements
\begin{frame}[standout]
    Demo time!
\end{frame}

% Review
% Conclusion
% Restate main message
% complement with other interpretations 
\begin{frame}{Review}
    \begin{itemize}
        \item Why?
        \item The parts%
              \begin{itemize}
                  \item Console
                  \item Amplifiers
                  \item Switch
                  \item Probe
              \end{itemize}
        \item Capture \& Process Software
        \item Experimental Results
        \item Demonstration
    \end{itemize}
\end{frame}
% We've understood why NMR is desirable
% We've gone through the concept of what it is
% We've step by step built the spectrometer from console, tx, rx, switch and probe
% We've now seen how a the software works and performed a measurement
% I hope I could convince you that the whole setup is working

\begin{frame}{Outlook}
    \begin{itemize}
        \item Shim Driver
        \item Shielding
        \item Improve any part individually%
              \begin{itemize}
                  \item Cheaper Magnet
                  \item Better Probe
                  \item Software (CIC compensation filter, frequency adjustment during pulse, \ldots)
              \end{itemize}
        \item Investigate temperature stability
        \item Sell it to NexMR (or do Photo-CIDNP ourselves)
    \end{itemize}
\end{frame}

% NuevoMR shims, sabr enterprises manget

% Close
\begin{frame}{}
    \begin{center}
        \note[item]{Circling back to the beginning, I would like to end with a quote by E.M. Purcell}
        \emph{
            \enquote{I have not yet lost that sense of wonder, and of delight, that this delicate motion should reside in all ordinary things around us, revealing itself only to him who looks for it.}

            \vspace{2\baselineskip}

            \enquote{There the snow lay around my doorstep --- great heaps of protons quietly precessing in the Earth's magnetic field.}
            % In that on the first snowy, silent night this winter you'll think of the quiet precessions in the earth's magnetic field.
        }
    \end{center}
    \hfill{}--- E.M.\ Purcell
    \note[item]{I would not have thought I would get a glimpse of this wonder that Purcell describes when starting my thesis here, but I'm glad I did.}
    \note[item]{And I hope none of you have lost it yet}
\end{frame}

% End: Show during questions
\begin{frame}{Thank you!}
    \begin{columns}
        \begin{column}{0.5\textwidth}
            \centering
            \includesvg[width=0.5\textwidth]{./images/logo_magnETHical.svg}
        \end{column}
        \begin{column}{0.5\textwidth}
            \centering
            Find everything on \\ \vspace*{\baselineskip}

            \includesvg[width=0.5\textwidth]{./images/gitlab_qrcode.svg}

            \url{https://github.com/M4a1x/nmr-spectrometer}
        \end{column}
    \end{columns}
\end{frame}

%%%%%%%%%%%%%%%%%%%%%%%%%%%%%%%%%%%%%%%%%%%%%%%%%%%%%%%%%%%%%%%%%%%%%%%%%%%%%%%
% Appendix / Backup Slides
%%%%%%%%%%%%%%%%%%%%%%%%%%%%%%%%%%%%%%%%%%%%%%%%%%%%%%%%%%%%%%%%%%%%%%%%%%%%%%%

\appendix

\begin{frame}[standout]
    Backup
\end{frame}

\begin{frame}{An amplifier is basically just a transistor}
    \centering
    \begin{columns}
        \begin{column}{0.5\textwidth}
            \begin{itemize}
                \item Transistor:\\voltage-controlled current source
                \item \(
                      \begin{aligned}[t]
                          \text{higher voltage} & \rightarrow{} \text{higher current}          \\
                                                & \rightarrow{} \text{higher voltage } V_{R_C} \\
                                                & \rightarrow{} \text{lower voltage } V_{CE}   \\
                                                & \rightarrow{} \text{\ang{180} phase shift}
                      \end{aligned}
                      \)
            \end{itemize}

        \end{column}
        \begin{column}{0.5\textwidth}

            \begin{circuitikz}
                \draw[nodes={align=center}]
                (0,0) node[npn](Q){}
                (Q.B) to[short,-o] ++(-0.5,0) node[left]{\(V_{in}\)}
                (Q.C) to[R,l=\(R_C\),v<=\(V_{R_C}\)] ++(0,2) node[vcc]{\(V_{CC}\)}
                (Q.C) to[short,*-o] ++(1,0) node[right]{\(V_{out}\)}
                (Q.E) node[ground]{}
                ([shift={(0.1,0)}]Q.E) to[open,v_<=\(V_{CE}\)] ([shift={(0.1,0)}]Q.C)
                ;
            \end{circuitikz}
        \end{column}
    \end{columns}
    \note[item]{We want cheap, so using a simple is the obvious first approach}
    \note[item]{Unfortunately there's a lot to do:%
        \begin{itemize}
            \item Input/Output Impedance Matching
            \item Bias Tee
            \item DC coupling
            \item stability calculations
            \item feedback
            \item temperature compensation (current feedback)
        \end{itemize}
    }
    \note[item]{A complete amplifier is quite expensive}
    \note[item]{Solution: Use monolithic (integrated) amplifier}
    \note[item]{Take care of heat dissipation (Class-A)}
\end{frame}

\begin{frame}{The passive approach leaked too much power}
    % TODO remind of why switch
    % zahlen - gefühl - 25mhz -> wellenlänge
    \centering

    \begin{circuitikz}
        \ctikzset{
            diode=empty,
            diodes/scale=0.8
        }
        \draw[nodes={align=center}]

        % tx diodes
        (0,0) node[left]{Transmit} to[short,o-*] ++(1,0) coordinate(tx)
        (tx) -- ++(0, 0.5) to[D] ++(1.5,0) -- ++(0,-0.5)
        (tx) -- ++(0,-0.5) to[D,invert] ++(1.5,0) -- ++(0, 0.5)
        to[short,*-] ++(1,0) coordinate(mid)

        % A/B
        (mid) node[below](A){A}
        (mid) to[short,*-o] ++(0,2) node[above]{Probe}
        (mid) -- ++(3,0) coordinate(b)
        (b) node[above](B){B}

        % rx diodes
        (b) to[short,-*] ++(0,-0.5) coordinate(rx)
        (rx) -- ++(-0.5,0) to[D] ++(0,-1.5) -- ++(0.5,0)
        (rx) -- ++(0.5,0) to[D,invert] ++(0,-1.5) -- ++(-0.5,0)
        to[short,*-] ++(0,-0.5) node[ground]{}

        (b) to[short, *-o] ++(1,0)
        node[right]{Receive}
        ;
        \draw[<->] (A.east |- B.west) -- (B.west);
        \draw ($(A.east|-B.west)!0.5!(B.west)$) node[above]{\(\frac{\lambda}{4}\)};
    \end{circuitikz}

    \note[item]{So called "video feedthrough"}
    \note[item]{Especially noise during reception phase, leaking through turned off amplifier}
    \note[item]{"Traditional" passive design by Lowe and Tarr}
    \note[item]{Leads to distortion of low-power pulses}
    \note[item]{Same design can be used with PIN-Diodes (effectively current-controlled resistor)}
    \note[item]{But PIN Diodes often need higher frequencies (mid MHz), size of intrinsic semiconductor}
\end{frame}

\begin{frame}{A transmission line transforms impedance}
    \begin{columns}
        \begin{column}{0.6\textwidth}
            \centering
            \only<2->{
                \movie[width=0.8\textwidth]{%
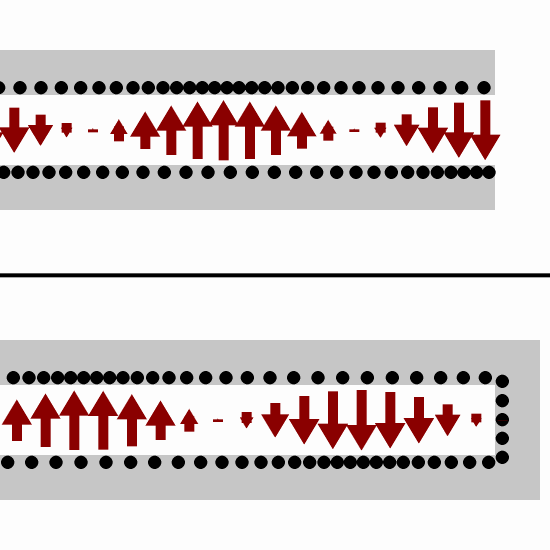
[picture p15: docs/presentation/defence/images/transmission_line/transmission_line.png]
                    
                }{transmission_line.gif}
            }
        \end{column}
        \begin{column}{0.4\textwidth}
            \vspace*{-0.5cm}

            \begin{circuitikz}
                \draw (0,0) to[short,o-] ++(-3,0) to[vsource,v=\(V_0\)] ++(0,2) to[R,l=\(Z_0\),-o] ++(3,0);
            \end{circuitikz}

            \vspace*{0.75cm}

            \hrule{}

            \vspace*{0.25cm}

            \begin{circuitikz}
                \draw (0,0) to[short,o-] ++(-3,0) to[vsource,v=\(V_0\)] ++(0,2) to[R,l=\(Z_0\),-o] ++(3,0);
                \draw (0,0) to[short,o-] ++(1,0) -- ++(0,2) to[short,-o] ++(-1,0);
            \end{circuitikz}
        \end{column}
    \end{columns}
\end{frame}

\begin{frame}{\(T_2\) Decay Animation}
    \begin{center}
        \movie[width=8.7cm,height=6.5cm]{}{./hahn_echo_decay_cc_gwm.gif}
    \end{center}
    \freefootnote{\href{https://commons.wikimedia.org/wiki/File:GWM_HahnEchoDecay.gif}{Gavin Morley --- CC BY-SA 3.0}}
\end{frame}

\begin{frame}{MaRCoS}
    \centering
    \vspace*{-1\baselineskip}
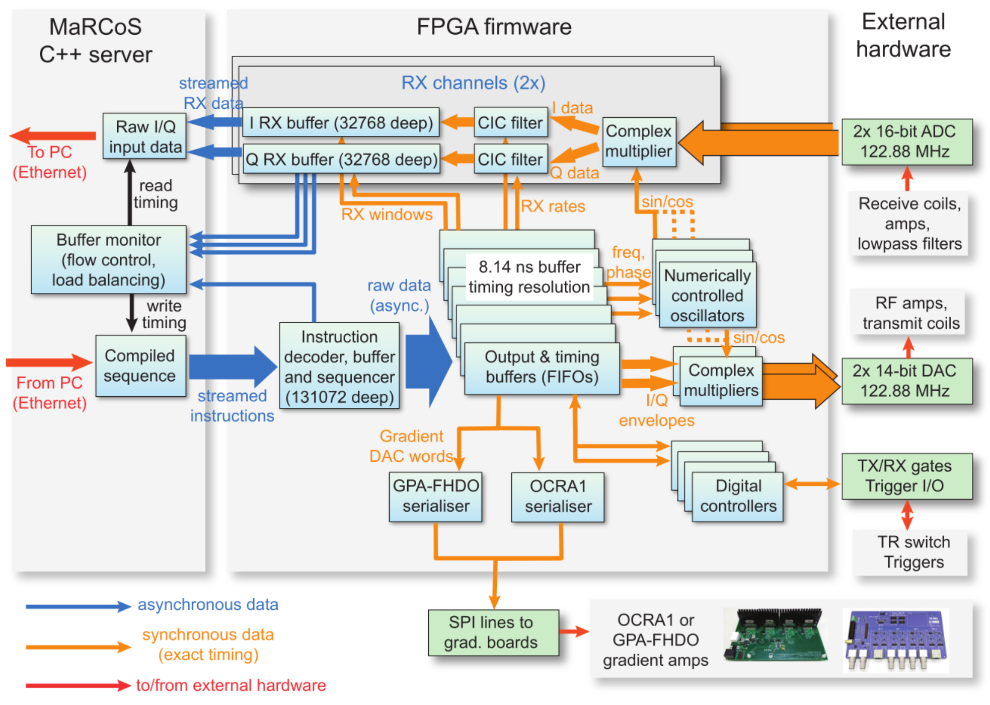
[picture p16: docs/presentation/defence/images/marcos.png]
    
\end{frame}

\end{document}

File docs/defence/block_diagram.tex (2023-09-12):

\documentclass{standalone}

% Fonts
\usepackage{fontspec}  % Requires LuaLaTeX
\usepackage{mathtools}  % Math
\usepackage[
  warnings-off={
      mathtools-colon,%
      mathtools-overbracket,%
    }
]{unicode-math}% Load after mathtools
\usepackage[tracking]{microtype}
\microtypesetup{protrusion=true,expansion=true}  % classicthesis

\setmainfont[Numbers=Lowercase,Scale=1.04]{TeX Gyre Pagella}
\setsansfont{Merriweather Sans}
\setmonofont[AutoFakeSlant,Scale=MatchLowercase]{inconsolata}
\setmathfont[mathrm=sym,mathit=sym,mathsf=sym,mathbf=sym,mathtt=sym,NFSSFamily=tgpl]{TeX Gyre Pagella Math}
\newfontfamily{\unitnumberfont}[Numbers=Uppercase]{Merriweather Sans}%TeX Gyre Pagella}  % Upright numbers for units in siunitx
\renewcommand{\familydefault}{\sfdefault}

\usepackage{pgfplots}		% Also loads Tikz
\pgfplotsset{compat=1.18}       % Set compatibility version. Can be updated as required
\usepackage{pgfplotstable}	% For advanced table calcs, e.g. 'y expr' to mathematically process input data:
\usepackage[edges]{forest}	% Comprehensive trees
\usepackage{tikz-3dplot}

% Only use libraries as needed to keep compilation times low
\usetikzlibrary{
  positioning,	% Relative positioning etc.
  calc,			% Calculate distances, coordinates etc.
  shapes, 		% For cross out
  backgrounds,	% Draw on background layer
  fit,			% Fit new node around existing coordinates
  decorations,
  arrows,
  arrows.spaced,
  intersections,
  trees,
  % circuits.ee.IEC,% Electrical engineering circuits lib
  patterns,
  3d,
  tikzmark,		% Marks/coordinates at arbitrary positions
}
\usepgfplotslibrary{
  colorbrewer,
  units,
  dateplot,
  fillbetween,
  groupplots,
}
\usepackage[european, siunitx]{circuitikz}

% Print a contour around letters, e.g. black text with a white border on some noisy
% background, so that text remains legible.
% NOT COMPATIBLE WITH XELATEX! Requires pdflatex or lualatex (our case)
\usepackage[outline]{contour}
\contourlength{0.12em}

\newcommand*{\ctrw}[1]{% Black text, white contour
  \hypersetup{hidelinks}% Hide links, which might be colored
  \contour{white}{\textcolor{black}{#1}}%
}%

\newcommand*{\ctrb}[1]{% White text, black contour
  \hypersetup{hidelinks}% Hide links, which might be colored
  \contour{black}{\textcolor{white}{#1}}%
}

\begin{document}
\begin{circuitikz}
    \ctikzset{bipoles/amp/width=0.9}
    \draw[nodes={align=center}]
    (0,0) coordinate(mid)

    % RP
    (mid) node[draw, minimum height=5.5cm, minimum width=2.5cm,label=Console](redpitaya){}
    (redpitaya.west) coordinate(inp) node[right]{Input}
    ($(redpitaya.east)!0.75!(redpitaya.north east)$) coordinate(rptx) node[left]{Transmit}
    ($(redpitaya.east)!0.75!(redpitaya.south east)$) coordinate(rprx) node[left]{Receive}

    % Computer
    (-3,0) node(seq){Sequence}
    (seq.east) -- (redpitaya.west) node[inputarrow]{} coordinate(console)

    % TX
    (rptx) to[lowpass,l=Lowpass,>] ++(3,0)
    to[amp,l=Amplifier,>] ++(3,0) coordinate(tx)

    % Circulator
    (mid -| tx) node[circulator,label={left:Switch}](circ){}
    (tx) -| (circ.n) node[inputarrow,rotate=270]{}

    % RX
    (rprx -| circ) coordinate(rx)
    (circ.s) |- (rx)
    (rx) to[amp,l=Amplifier,>] ++(-3,0)
    to[lowpass,l=Lowpass,>] ++(-3,0) node[inputarrow,rotate=180]{}

    % Probe
    (circ.e) -- ++(1,0)
    node[dinantenna](probe){}
    node[below=1ex]{Coil}
    ;
\end{circuitikz}
\end{document}

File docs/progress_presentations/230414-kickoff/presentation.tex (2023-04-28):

\documentclass{ethpresentation}

\begin{document}
  \maketitle
  % \section{First Section}
  \begin{frame}{Our goal is a functioning low-field\\NMR benchtop spectrometer}
    \begin{figure}
      \centering
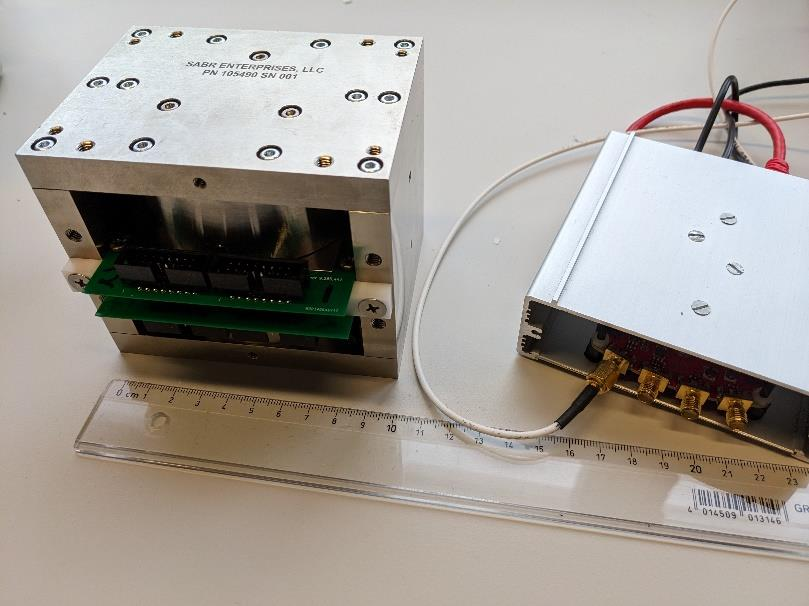
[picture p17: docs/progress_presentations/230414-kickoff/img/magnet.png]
      
    \end{figure}
  \end{frame}
  \begin{frame}{We've made a probe holder\\and an RF-coil already}
    \begin{columns}
      \begin{column}{0.45\textwidth}
        
      \end{column}
      \begin{column}{0.45\textwidth}
        
      \end{column}
    \end{columns}
  \end{frame}
  \begin{frame}{Next we will setup the console, measure the magnetic field\\and build, match and tune the probe}
    \begin{columns}
      \begin{column}{0.33\textwidth}
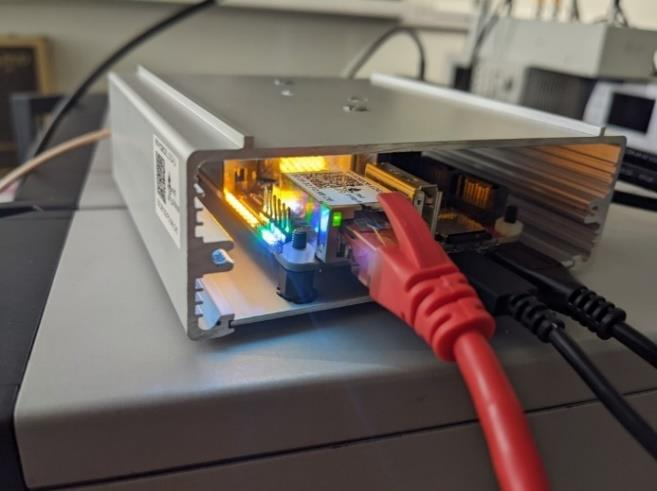
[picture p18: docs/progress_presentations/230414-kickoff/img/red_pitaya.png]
        
      \end{column}
      \begin{column}{0.33\textwidth}
        \centering
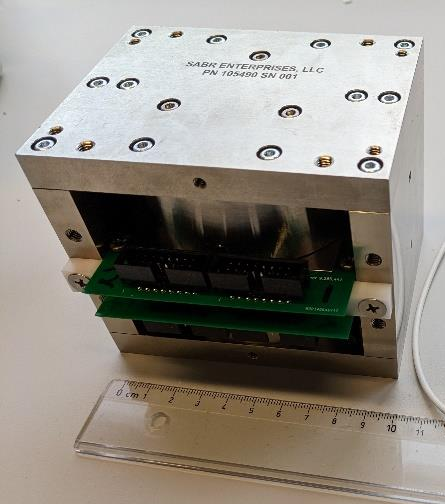
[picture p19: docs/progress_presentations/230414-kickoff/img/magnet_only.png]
        
      \end{column}
      \begin{column}{0.33\textwidth}
        
      \end{column}
    \end{columns}
  \end{frame}
  \begin{frame}[standout]
    Thank you!
  \end{frame}
  \appendix
  % \begin{frame}[standout]
  %   A backup graph for explaining things.
  % \end{frame}
\end{document}

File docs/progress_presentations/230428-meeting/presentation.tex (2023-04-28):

\documentclass{ethpresentation}

\title{Building a 25 MHz NMR Spectrometer}
\date{\today}
\author{Maximilian Stabel}
\institute{ETH Zürich}

\begin{document}
  \maketitle
  % \section{First Section}
  \begin{frame}{Since last time}
    \begin{columns}
      \begin{column}{0.45\textwidth}
        \begin{itemize}
          \item Meeting with Christian Vogt
          \item Finished building probe
          \item Tune \& Match probe
          \item Explored measurement setup
          \item Thought about power supply
        \end{itemize}
      \end{column}
      \begin{column}{0.45\textwidth}
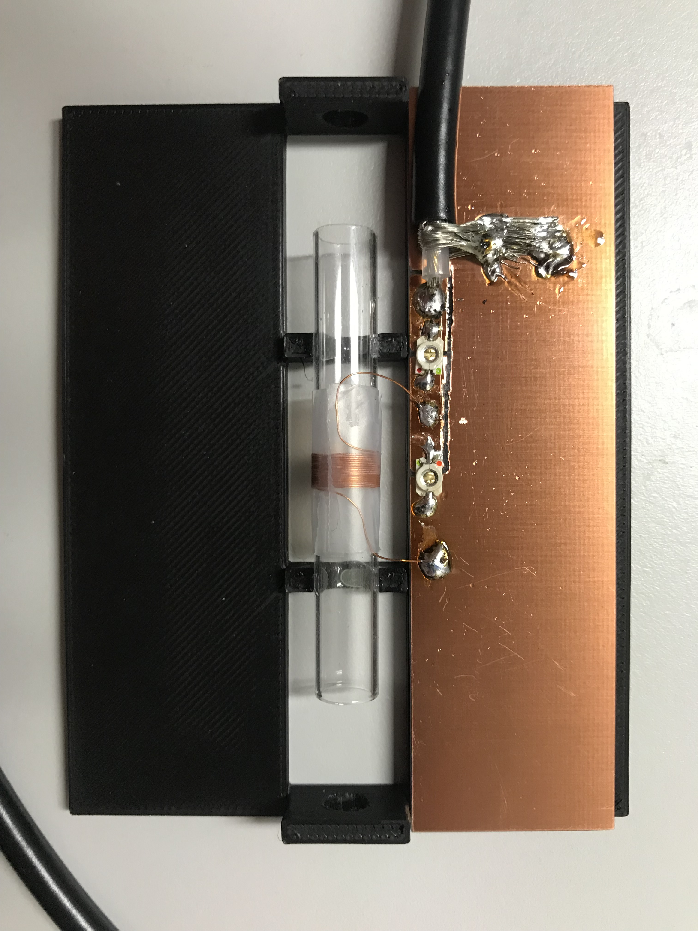
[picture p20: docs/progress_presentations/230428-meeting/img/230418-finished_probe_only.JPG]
        
      \end{column}
    \end{columns}
  \end{frame}
  \begin{frame}{Upcoming}
    \begin{itemize}
      \item Setup/Assemble spectrometer
      \item Measure water with probe v1
      \item Come up with single channel design for current source
      \item Simulate single channel
    \end{itemize}
  \end{frame}

  % \begin{frame}[standout]
  %   Thank you!
  % \end{frame}

  % \appendix
  % \begin{frame}[standout]
  %   A backup graph for explaining things.
  % \end{frame}
\end{document}

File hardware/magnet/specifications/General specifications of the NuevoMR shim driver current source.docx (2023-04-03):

General specifications of the NuevoMR shim driver current source

2022-12-01

The NuevoMR active shim design is highly matrixed, requiring 32 independently adjustable currents to produce the harmonic homogeneity correction fields. The design emphasizes minimal use of gap space inside the magnet, at the cost of complexity in the electronics outside the magnet.

At NuevoMR, we have successfully used a simple prototype multichannel current source for more than 5 years. Although this design has a number of shortcomings rendering it unsuitable for commercialization, it does provide data to support the following current source specification:

Number of independent channels: 32

Maximum current per channel: ± 0.5 A

Current output supply rail voltage: ± 2.5 V (for typical shim sets)

Total supply rail current: 3A each (in some rare cases, this is too low)

Notes:
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

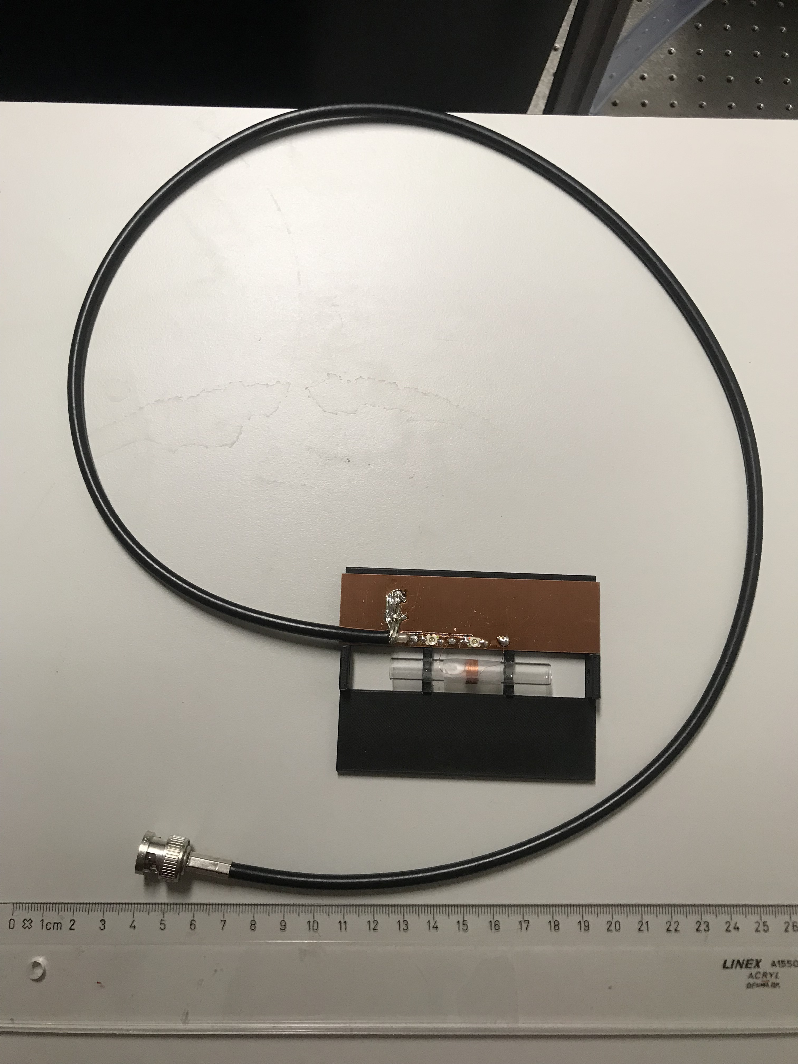
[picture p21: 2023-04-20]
hardware/probe/probe_holder_v1/pictures/230418-finished_probe_full.JPG

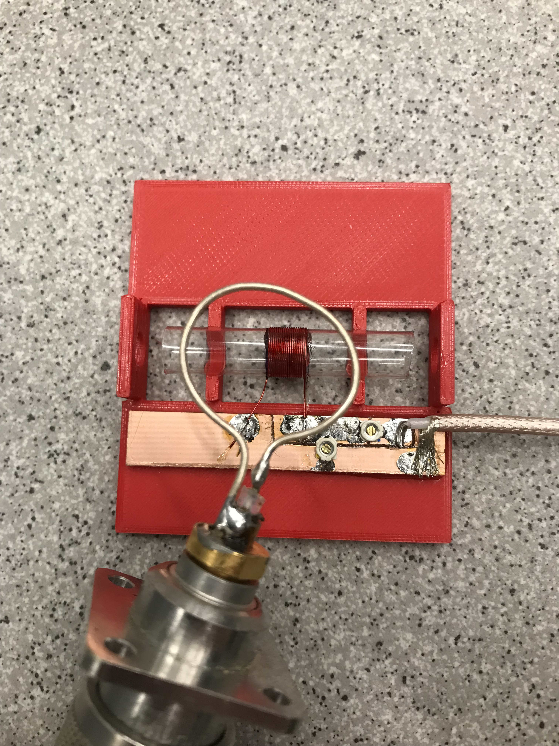
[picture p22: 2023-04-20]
hardware/probe/andrew/pictures/230419-pickup_coil_near_andrew_probe.JPG

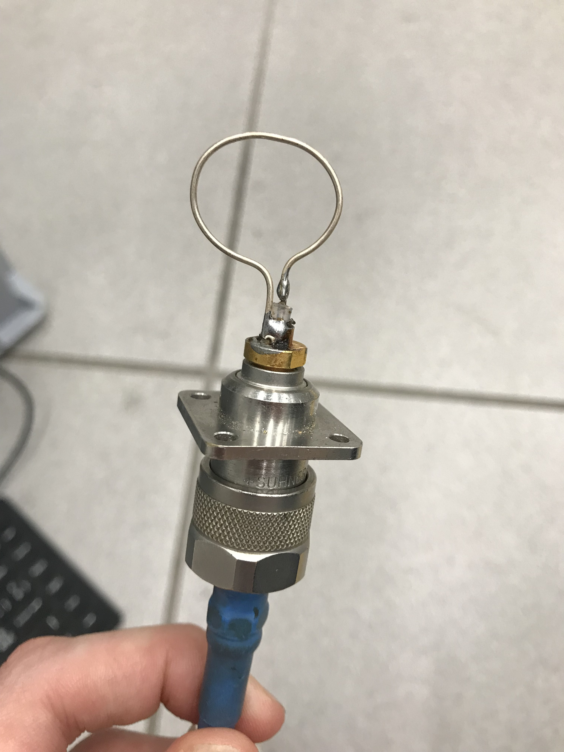
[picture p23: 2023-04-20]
hardware/probe/probe_holder_v1/pictures/230419-pickup_coil.JPG

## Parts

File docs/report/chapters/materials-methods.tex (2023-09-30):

\setchapterpreamble[u]{%
    \margintoc\hfil
    \dictum[Richard Feynman]{What I cannot create,\\I do not understand.}
}

% Methods
\chapter{The spectrometer}
\labch{methods}
% Write in theorem-proof fashion

The individual parts of the spectrometer have been designed with several goals in mind. The main guiding principle was reproducibility and availability such that anyone can reproduce the build with minimal effort. All the necessary steps are documented below, including the reasoning for steps not taken. For verification and testing of the parts below the console (see \refsec{console}) itself may be used\sidenote{Instruction for using the RedPitaya as an \gls{lcrmeter}, \acrshort{vna}, or spectrum analyser can be found in its documentation}. A more practical solution is using separate devices for this to avoid the reconfiguration hassles. The open-source NanoVNA-H4\sidenote{\approx{}60CHF, \url{https://nanovna.com/}} \acrshort{vna} and the tinySA\sidenote{\approx{}50CHF, \url{https://tinysa.org/}} spectrum analyser are affordable and at these frequencies very capable alternatives to expensive lab equipment. They have been used extensively during the development of the hardware.

The following sections describe the design and build process --- including the reasoning behind the decisions taken --- of the \magnethical{} NMR spectrometer. \reffig{block-diagram} shows an overview schematic of the main components that will be discussed.

In general, the components were selected to be standard parts wherever possible. RF electronics are highly sensitive to stray capacitances and inductances, therefore most dedicated RF components use surface mount\sidenote{as opposed to through-hole (SMT)} (SMD) technology, sometimes even without pins. The passive components, like inductors, capacitors and resistors are in 0805\sidenote{0805 means \qty{0.08}{in} x \qty{0.05}{in}. PCB design is a mess of different unit systems, e.g. board sizes are often given in \unit{\milli\metre} whereas trace width is often given in \unit{mil} (thousandth of an \unit{in}). Rarely 0805 is written as 2012M: \qty{2.0}{\milli\metre} x \qty{1.2}{\milli\metre}} sizing, which was deemed large enough to be still easy to solder by hand. All traces were impedance matched to \qty{50}{\ohm} on standard \qty{1.6}{\milli\metre} FR4 cards, milled with standard drill sizes to facilitate the use of affordable standard manufacturing processes. Lastly, SMA connectors were chosen for their small footprint and secure screw connection, as opposed to BNC connectors (large) and SMB connectors (less secure connection). Most parts were searched for using the parametric search functionality of the big distributors and filtered for only active, available and stocked parts --- a rather large restriction in times of a global chip shortage.

\begin{figure}[hbt]
    \centering
    
    \caption{\captiontitle{Block Diagram.} The main components of the \magnethical{} NMR spectrometer, include the console, lowpass filters, analogue amplifiers, transmit-receive switch and transmit-receive coil.}
    \labfig{block-diagram}
\end{figure}

In line with the goal of an accessible NMR spectrometer, the built spectrometer is very affordable. \reftab{total-comparison} shows a comparison of it with a high-field spectrometer and other commercial benchtop spectrometers capable of measuring samples in a \qty{5}{\milli\metre} NMR tube in terms of features.

\begin{table}
    \caption{\captiontitle{Comparison of different NMR spectrometer types.} Prices are estimates based on previous purchases of the lab and experience in the price developments across vendors.}
    \begin{tabular}{@{} lrrr @{}}
        \toprule
                                       & Superconducting                        & Benchtop                            & \magnethical{}                                          \\
        \midrule
        Price [k\,CHF]                 & \numrange[range-phrase=--]{200}{18000} & \numrange[range-phrase=--]{50}{150} & \approx\num{10}                                         \\
        Frequency [\unit{\mega\hertz}] & \numrange[range-phrase=--]{300}{1200}  & \numrange[range-phrase=--]{40}{125} & \num{25}                                                \\
        Resolution [\unit{\hertz}]     & \approx\num{0.2}                       & \numrange[range-phrase=--]{0.2}{1}  & \approx \num{2.5}/\num{50}\footnote{with/without shims} \\
        Weight [\unit{\kilo\gram}]     & \numrange[range-phrase=--]{600}{15000} & \numrange[range-phrase=--]{25}{150} & \approx\num{5}                                          \\
        \bottomrule
    \end{tabular}
    \labtab{total-comparison}
\end{table}

\reftab{prices} shows a more detailed record of the prices of the individual components used and described in the following chapters. The vast majority of the money is spent on the magnet. Further development should seek better pricing here or start looking into home-made alternatives.

\begin{table}
    \caption{\captiontitle{Prices of the individual parts of the built spectrometer in comparison.} Prices include \acrshort{vat} in \acrshort{chf}}
    \begin{tabular}{@{}
            l
            S[table-format=7.0,table-align-text-pre=false]
            S[table-format=3.2,table-align-text-pre=false]
            S[table-format=5.2,table-align-text-pre=false]
            @{}}
        \toprule
                        & {\qty{600}{\mega\hertz}\footnote{estimated costs}} & {mini-circuits} & {\magnethical}          \\
        \midrule
        Power Amplifier & 50000                                              & 323.49          & 36.01                   \\
        Switch          & {-}                                                & 82.06           & 20.05                   \\
        Probe           & 100000                                             & {-}             & {\approx{}} 15.00       \\
        \acrshort{lna}  & 50000                                              & 409.38          & 73.11                   \\
        Shim Driver     & {-}                                                & {-}             & 257.08                  \\
        Console         & 200000                                             & {-}             & 662.53                  \\
        Magnet          & 1000000                                            & {-}             & {\approx{}} 9000.00     \\
        \bottomrule
        \textbf{Sum}    &                                                    &                 & \textbf{\num{10142.80}} \\
    \end{tabular}
    \labtab{prices}
\end{table}

The section order follows the path of the signal, that is, clockwise around the schematic starting with the console.

\section{The console}
\labsec{console}
\begin{marginfigure}
    
    \labfig{block-diagram-console}
\end{marginfigure}

The relatively low frequency of \(f_0 = \qty{25}{\mega\hertz}\)\sidenote{Given by the \ch{^1H} resonance frequency in the \qty{0.6}{\tesla} magnet} as well as the low bandwidth of only about \qty{10}{ppm}\sidenote{Equals \qty{250}{\hertz} at \qty{25}{\mega\hertz}} of the expected signal allows moving a lot of previously analogue tasks into the digital domain, greatly simplifying the hardware setup and making it more flexible. According to the Nyquist theorem, the minimum frequency that can be used to digitize an analogue signal without loss of information\sidenote{That is, without aliasing issues} must be more than twice as large as the highest frequency component of interest in the signal. In our case, the analogue-to-digital conversion must happen with more than
\[
    f_{min} \ge 2f_0 = \qty{50}{\mega\hertz}
\]
if oversampling is to be used. The setup could also make use of the low bandwidth of the signal and use the aliasing effect of the analogue-to-digital conversion to its advantage using undersampling. Since this requires taking further care when sampling and filtering, and the expected frequencies are low enough to make oversampling feasible, oversampling is employed in this setup. This has the added advantage of higher flexibility since the sampling frequency can be easily adjusted downwards.

For digital processing, a \acrfull{fpga} is used, which can be thought of as a piece of programmable hardware. They have been successfully used in \acrshort{nmr} spectrometers since 2007 to enable pulse generation and processing \sidecite{takedaHighlyIntegratedFPGAbased2007}. To ease development a ready-made \acrshort{fpga} board --- the RedPitaya SDRlab 122-16 shown in \reffig{redpitaya} --- was chosen. With a sampling frequency of \qty{122.88}{\mega\sample\per\second} it is well above the Nyquist limit. Combined with a resolution of \qty{16}{bit} it is more than capable of capturing all relevant data from the analogue signal. Due to the commercial nature, the board is easily procured directly from RedPitaya or any of the well-known distributors\sidenote{For example Digikey, Mouser, Farnell, \dots}. A possible open-source alternative in the future would be the LimeSDR\sidenote{\url{https://limemicro.com/products/boards/limesdr/}}. With a sampling frequency of \qty{61.44}{\mega\sample\per\second}, limited by the USB3 interface, and a resolution of \qty{12}{bit} it is less powerful than the RedPitaya, but still fast enough for oversampling without loss of information. This board would cost less than half (\approx 280CHF) of the RedPitaya board and would enable a completely open design of the spectrometer --- in line with the accessibility goals of this work. Unfortunately, due to the young age of this project and the crowd-sourced nature, no board was available for purchase at the time of writing.

\begin{figure}[hbt]
    \centering
    
    \caption{\captiontitle{RedPiaya SDRlab 122-16.} 3D rendering of the console in KiCAD. Can be thought of as an \enquote{RF Raspberry Pi}. It has a Dual Core ARM Cortex A9, \qty{512}{\mega\byte} RAM, Gigabit Ethernet, 2x transmit, 2x receive, an ADC sample rate of \qty{122.88}{\mega\sample\per\second}, \qty{16}{\bit} resolution, a bandwidth of \qty{300}{\kilo\hertz} to \qty{550}{\mega\hertz} and a voltage range of \qty{0.5}{\vpp}/\qty{-2}{\deci\belm} (\qty{50}{\ohm}). The DAC has the same sample rate and voltage range, but a resolution of \qty{14}{\bit} and a bandwidth of \qty{300}{\kilo\hertz} to \qty{60}{\mega\hertz}.}
    \labfig{redpitaya}
\end{figure}

After sampling the signal is demodulated using a quadrature detection system by multiplying it with the signal of a complex numerically controlled local oscillator. The same principle is applied inversely on the sending side for modulation. The resulting complex demodulated signal is then passed through a \acrfull{cic} filter for low-pass filtering and decimation to filter out high-frequency components of the signal and reduce the size of the data stream. The full data steam would incur a bandwidth of
\[
    \qty{16}{\bit} \cdot \qty{122.88}{\mega\sample\per\second} = \qty{245.76}{\mega\byte\per\second}
\]
per channel. With potentially 2 transmit and 2 receive channels this results in a data rate of close to \qty{1}{\giga\byte\per\second}, which is way higher than the theoretical limit of \qty{116}{\mega\byte\per\second} of the Ethernet interface. Due to inefficiencies in the Linux kernel of the RedPitaya Image, the practical data rate limit for continuous streaming is a lot lower at about \qty{20}{\mega\sample\per\second}\sidenote{According to the official \gls{lcrmeter} documentation (\url{https://redpitaya.readthedocs.io/en/latest/appsFeatures/applications/streaming/appStreaming.html})}. This has been improved in Pavel Demin's kernel image, where speeds up to \qty{80}{\mega\byte\per\second} have been measured\sidenote{\url{https://pavel-demin.github.io/red-pitaya-notes/alpine/}}. However, this only becomes relevant on long acquisition times over several seconds and has not been thoroughly tested as it has not been relevant, yet.

All of these digital signal-processing tasks are performed by the \acrshort{marcos} \acrshort{fpga} firmware developed by Vlad Negnevitsky\sidecite{negnevitskyMaRCoSOpensourceElectronic2023}. The system is designed for a low-field MRI system but could be easily adapted for NMR spectroscopy. The demodulated, filtered and decimated data from MaRCoS is then sent through its C server to the developed high-level Python interface. \reffig{marcos} shows an overview of the \acrshort{marcos} architecture. For more information on the Python programming interface see \refsec{software}.

\begin{figure}[hbt]
    \centering
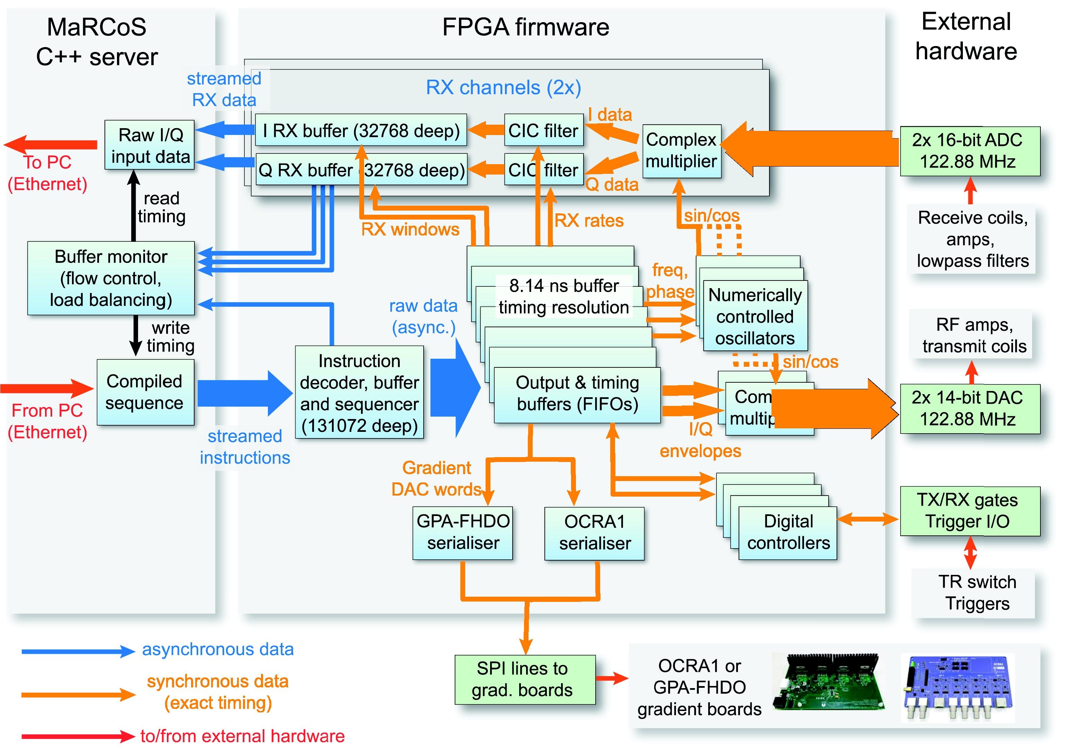
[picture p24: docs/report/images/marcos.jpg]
    
    \caption{\captiontitle{MaRCoS system architecture.} \enquote{The server receives a sequence from the client PC via Ethernet and streams it to the FPGA firmware, where it is translated into time-synchronous hardware operations including RF and gradient outputs. The firmware receives data from the ADCs, demodulates and filters it, and saves it into RX buffers, from which it is read by the server and sent to the PC} (\cite{negnevitskyMaRCoSOpensourceElectronic2023}, Figure 3) Magnetic field gradients are not necessary for spectroscopy and thus not used.}
    \labfig{marcos}
\end{figure}

The low-noise amplifiers before the receive inputs can output more than \qty{+20}{\deci\belm} of power (\refsec{low-noise-amplifier}). The maximum input the \acrshort{rp} can handle before breaking is \qty{1}{\vpp}/\qty{+4}{\deci\belm}. Thus in case any \acrshort{rf} signal gets leaked into the cascaded amplifier chain the inputs of the \acrshort{rp} could be destroyed. To prevent this a pair of crossed shunt diodes is connected before the inputs.

The first obvious choice for this would be standard silicon diodes with a threshold voltage of about \qty{0.7}{\volt}. The prototype with the standard BAV99 diodes would only clamp the signal safely to about \qty{2}{\vpp}. The lower threshold voltage BYS10 Schottky diodes tried next behaved attenuated the signal by about \qty{12}{\deci\bel}. The oscilloscope recording of a \qty{100}{\milli\vpp} sine wave of a function generator passed through the Schottky diodes is shown in \reffig{input-protection-attenuation}.

\begin{figure}[hbt]
    \centering
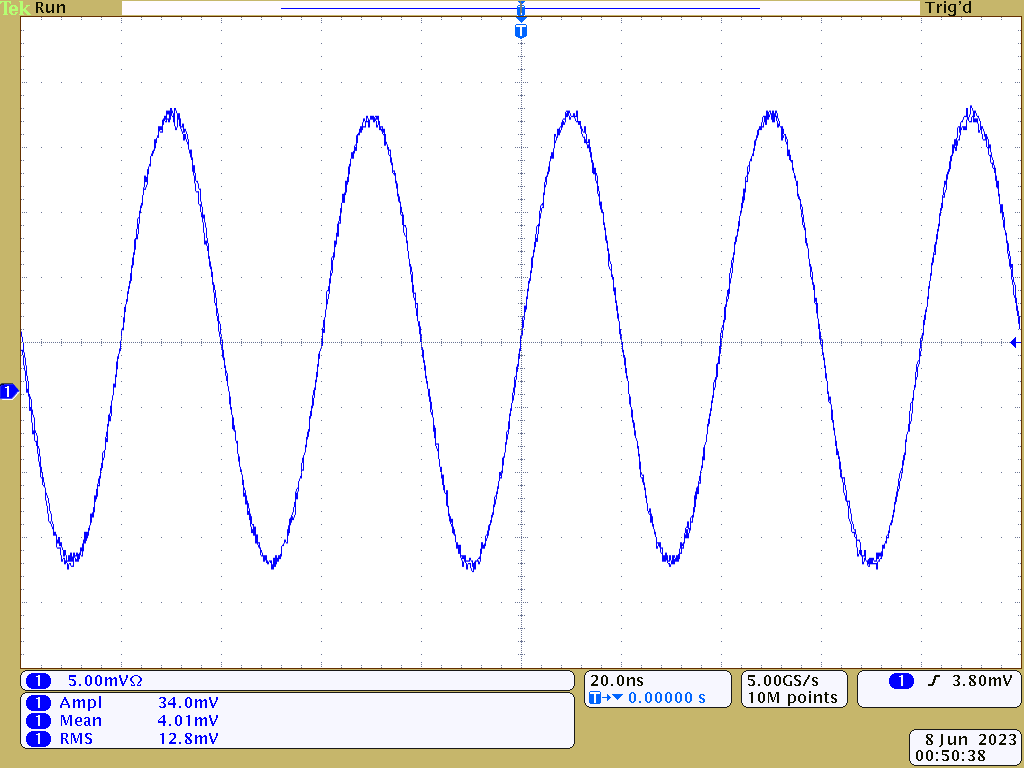
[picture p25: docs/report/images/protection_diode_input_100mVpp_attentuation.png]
    
    \caption{\captiontitle{Receive input protection of crossed shunt BYS10 Schottky diodes attenuating the signal.} The attenuation is unacceptably high. The input signal of \qty{100}{\milli\vpp} is attenuated down to \qty{24}{\milli\vpp} or by about \qty{12}{\deci\bel}.}
    \labfig{input-protection-attenuation}
\end{figure}

A simulation confirmed later by measurement shows a phase shift between input and output occurs. This lead to the hypothesis that a high capacitance forming a filter with the \qty{50}{\ohm} termination is responsible for the attenuation of the signal. Through a parameterized search the RB520SM-30 Schottky diode was found and then simulated to be suitable for the input protection. The measurement of the final version can be found in \reffig{input-protection-working}. While still attenuating the signal, only about \qty{1.4}{\deci\bel} are lost while still clamping the maximum voltage to less than \qty{1}{\vpp}.
\begin{figure}[!hbt]
    \centering
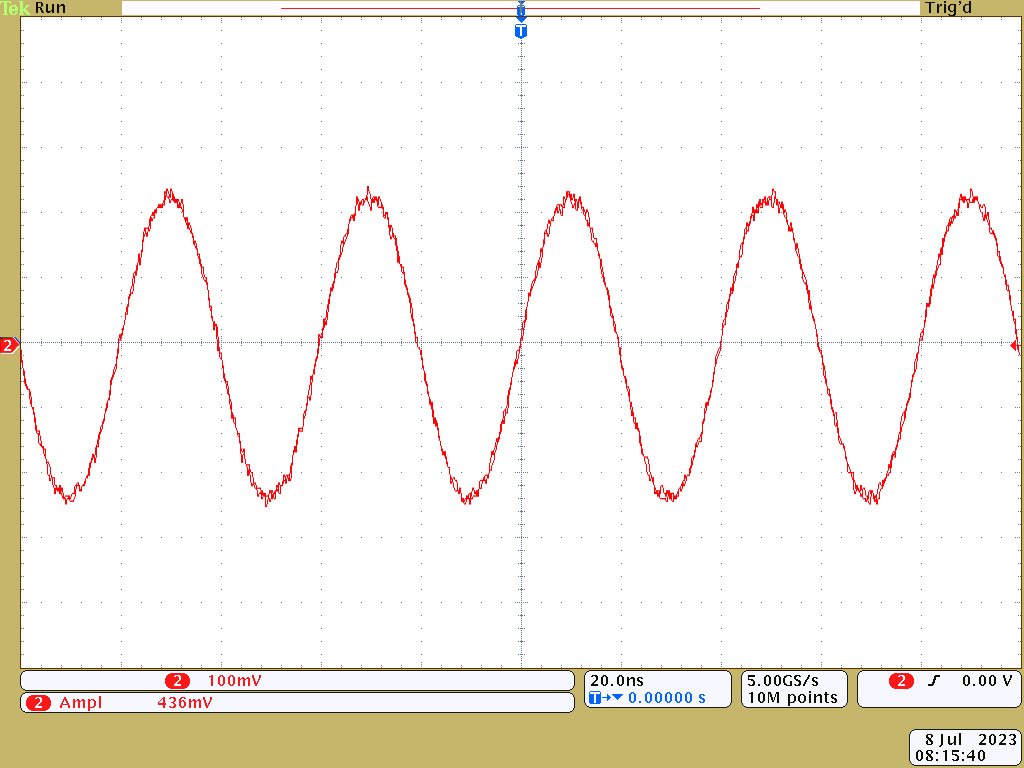
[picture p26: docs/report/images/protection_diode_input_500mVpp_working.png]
    
    \caption{\captiontitle{Working receive input protection of crossed shunt RB520SM-30 Schottky diodes.} The Schottky diodes attenuate the \qty{500}{\milli\volt} input signal to about \qty{426}{\milli\volt}, equivalent to a power attenuation of \qty{1.4}{\deci\bel}.}
    \labfig{input-protection-working}
\end{figure}

\section{The power amplifier}
\labsec{poweramp}
The power amplifier has to amplify the low-power digitally synthesised signal from the console. The console described in \refsec{console} above has a maximum output power of \qty{0.5}{\volt} or \qty{-2}{\deci\belm} into a \qty{50}{\ohm} load.
\begin{marginfigure}[-4\baselineskip]
    
    \labfig{block-diagram-pa}
\end{marginfigure}

The output power required to excite a volume of \qty{1}{\centi\meter\cubed} on a bandwidth of about \qty{10}{\kilo\hertz} or \qty{20}{ppm} in a high field magnet (\qty{500}{\mega\hertz} (\ch{^1H})/\qty{11.7}{\tesla}) is about \qty{11}{\watt} \sidecite{louis-josephDesigningBuildingLowcost2019}. The magnet in this work (see \refsec{magnet}) has a field strength of \qty{25}{\mega\hertz} (\ch{^1H})/\qty{0.6}{\tesla}, therefore \qty{20}{ppm} equals an excitation bandwidth of only \qty{500}{\hertz}. The sample volume is only \(\qty{100}{\micro\litre} = \qty{0.1}{\centi\meter\cubed}\) as well, reducing the required energy further.

Targeting a pulse length of \qty{20}{\micro\second} for a \ch{^1H} \(\frac{\pi}{2}\)-pulse the RF pulse needs to generate a magnetic field of about
\[
    B = \frac{\alpha}{\gamma\tau} = \frac{\frac{\pi}{2}}{\qty{42.577}{\mega\hertz\per\tesla}\cdot{}\qty{20}{\micro\second}} = \qty{1.845}{\milli\tesla}
\]

The magnet has a homogenous region of \(\qty{100}{\micro\litre}\) for a \qty{5}{\milli\meter} NMR tube, resulting in an NMR active length of about \(l = \qty{6}{\milli\meter}\). If we assume a simple solenoid of that length with about \(n = 20\) turns, a Q factor of 100 (usually in the range of 10 to 1000 \cite{mispelterNMRProbeheadsBiophysical2015}) and a self-inductance of \(L = \frac{\mu_0n^2A}{l} = \qty{3}{\micro\henry}\) we can roughly estimate the required peak power \(P\) with the following formulas \sidecite{mispelterNMRProbeheadsBiophysical2015}
\begin{align}
    B & = \frac{\mu{}_0nI}{l}              \\
    P & = R\underbar{I}^2 = R\frac{I^2}{2} \\
    Q & = \frac{L\omega}{R}                \\
\end{align}
where \(B\) is the magnet field produced by the current \(I\) through a solenoid of length \(l\) with \(n\) windings and and air core of permittivity \(\mu{}_0\). \(P\) is the maximum power pushed into the solenoid by current \(I\) over resistance \(R\) and \(Q\) is the definition of the quality factor for a self-inductance \(L\) and resistance \(R\). Putting it all together results in an estimated power level of
\begin{align}
    P & = \frac{B^2l^2L\omega}{2\mu{}_0^2n^2Q}                                                                                                                                              \\
      & = \frac{(\qty{1.845}{\milli\tesla})^2 \cdot (\qty{6}{\milli\metre})^2 \cdot \qty{3}{\micro\henry} \cdot 2\pi{} \cdot \qty{25}{\mega\hertz}}{2 \cdot \mu{}_0^2 \cdot 20^2 \cdot 100} \\
      & = \qty{457.12}{\milli\watt}
\end{align}

The exact power required is difficult to calculate at best due to various losses of the materials, the sample, the surrounding materials and losses due to radiation. Previous works with low-field NMR spectrometers used power amplifiers with a maximum power output of \qty{1}{\watt}\cite{chenUltralowCostNMR2015} and \qty{5}{W}\cite{louis-josephDesigningBuildingLowcost2019}. Lower power RF amplifiers have the advantage of lower required voltages, lower noise, less cooling requirements and simpler integrated designs.

The most affordable option for the power amplification would be based on \acrshort{rf} transistors. Unfortunately, this also necessitates an involved design process including not only biasing and feedback design, but also impedance matching and power supply circuits of a possible multi-stage power amplifier. This alone could be the topic of another thesis. Therefore, an \acrshort{mmic} approach has been chosen. Furthermore, availability in the \qty{1}{\watt} range is large due to a large commercial market in this power range especially for CATV amplifiers. Therefore, a \qty{1}{\watt} \acrshort{mmic} amplifier was chosen.

The \acrfull{mmic} amplifier has biasing, possible feedback and stabilization requirements all integrated on a single substrate design. In an application only power, \acrshort{dc} blocking in addition to adequate cooling have to be supplied, since this is a Class A amplifier design.

The final board can be found in \reffig{poweramp}, with its schematic in the appendix \refsec{poweramp-schematic} and the part list in \refsec{poweramp-parts}.

\begin{figure}[hbt]
    \centering
    
    \caption{\captiontitle{\acrshort{rf} power amplifier.} 3D rendering of the power amplifier \acrshort{pcb} in KiCAD. The signal travels from left to right with the power supply circuitry above. It contains two \acrshort{mmic} amplifier stages, the AD5536 and the PHA-202+. A \qty{-6}{\deci\bel} attenuator was added in between and a passive low-pass filter in front (\(f_c = \qty{35}{\mega\hertz}\)). \(G \approx \qty{32}{\deci\bel}\), \(P_{\qty{1}{\deci\bel}} \approx \qty{+30}{\deci\belm}\)}
    \labfig{poweramp}
\end{figure}

The signal from the RedPitaya travels left to right through a low pass, the pre-amplifier, an attenuator and the power amplifier. The parts at the top of the board are standard linear voltage regulators used for stabilizing the voltage from the external DC supply. The power amplifier chip itself can be switched off by cutting the voltage supply.

The low-pass input filter functions as a digital reconstruction filter, smoothing the digitally synthesised waveform by filtering out high-frequency components of the signal left over from the switching of the FPGA and the zero-order hold DAC chip. It is a passive Chebyshev low-pass LC ladder filter realized with three 0805-sized SMD components.

The power amplifier is a PHA-202+, chosen for its easy powering requirements, \qty{50}{\ohm} matching and wide availability. However, it does not have enough gain (\qty{18.3}{\deci\bel})) to take the signal from \qty{-2}{\deci\belm} all the way to \qty{+30}{\deci\belm}. The missing \qty{14}{\deci\bel} in amplification are provided by the preamp (\qty{20}{\deci\bel}) minus the following attenuator (\qty{6}{\deci\bel}).

The AD5536 pre-amplifier is a \qty{50}{\ohm} matched, widely available \qty{20}{\deci\bel} gain GaAs gain block from Analog Devices. It is in an easy-to-solder package and has a low enough frequency specification to work with \qty{25}{\mega\hertz}. Alternatives with this gain and power are often difficult to solder due to the leadless design, unmatched (e.g. AFIC901N) \qty{75}{\ohm} matched (e.g. MAAL-011139) and often cannot amplify such a slow signal (e.g. TAT7430B, starting at \qty{50}{\mega\hertz}).

The \qty{6}{\deci\bel} resistive attenuator in between the amplifiers is realized as a \(\pi\)-circuit similar to the low pass ladder filter. It is used to stabilize the adjacent amplifiers and will dampen any oscillations that might occur due to load or stray capacitances or inductances. If necessary the attenuation could be reduced to e.g. \qty{3}{\deci\bel} to increase the maximum power output of the amplifier, however, since the \(P_{\qty{1}{\deci\bel}} = \qty{29}{\deci\belm}\) for the PHA-202+ it will not grow linearly. The potential distortions should be of little consequence for the transmission signal.

For blocking the DC bias current for the amplifiers simple 0805 100nF caps are used in series as a high pass filter. For a \qty{50}{\ohm} system we can calculate the minimum value for the capacitors using the standard formula \(X_C = \frac{1}{2\pi{}fC}\) and keeping in mind that the block is loaded on both sides thus \( 2 \cdot \qty{50}{\ohm} = \qty{100}{\ohm}\). For \qty{25}{\mega\hertz} we thus get a minimum capacitance of
\[
    C = \frac{1}{2\pi{}fX} = \frac{1}{2\pi{} \cdot{} \qty{25}{\mega\hertz} \cdot{} \qty{100}{\ohm}} = \qty{63.7}{\pico\farad}
\]
The chosen \qty{100}{\nano\farad} are significantly larger and simply chosen for convenience and availability. Their high-pass cut-off frequency is at
\[
    f = \frac{1}{2\pi{}XC} = \frac{1}{2\pi{} \cdot{} \qty{100}{\ohm} \cdot{} \qty{100}{\nano\farad}} = \qty{15.9}{\kilo\hertz}
\]
For the chosen capacitors\sidenote{C0805C104J5RACTU} by KEMET this can be easily verified using the provided K-SIM simulator\sidenote{\url{https://ksim3.kemet.com/capacitor-simulation}}, which confirms an insertion loss (S21) of \qty{0}{\deci\bel} and an input reflection (S11) of \qty{-68}{\deci\bel} for \qty{25}{\mega\hertz}.

\section{The switch}
\begin{marginfigure}
    
    \labfig{block-diagram-switch}
\end{marginfigure}

The switch has two main functions:
\begin{enumerate*}
    \item Protecting the receive path from the high power pulses when transmitting and
    \item blocking the noise of the transmit power amplifier when receiving.
\end{enumerate*}
The simplest approach for the user would be a passive switch, that does not need an active signal and simply forwards everything from the transmit port to the probe and everything from the probe to the receive port and nothing else. The possibly most popular design is the passive switch presented in \sidecite{loweFastRecoveryProbe1968} and pictured in \reffig{passive-switch-schematic}. It is based on easy-to-build, cheap and passive. On the downside, it has a narrow bandwidth, which is not a problem for our case, as the resonance frequency of the permanent magnet is fixed and varies only slightly.

\begin{figure}[hbt]
    \centering
    \begin{circuitikz}
        \ctikzset{
            diode=empty,
            diodes/scale=0.8
        }
        \draw[nodes={align=center}]

        % tx diodes
        (0,0) node[left]{Transmit} to[short,o-*] ++(1,0) coordinate(tx)
        (tx) -- ++(0, 0.5) to[D] ++(1.5,0) -- ++(0,-0.5)
        (tx) -- ++(0,-0.5) to[D,invert] ++(1.5,0) -- ++(0, 0.5)
        to[short,*-] ++(1,0) coordinate(mid)

        % A/B
        (mid) node[below](A){A}
        (mid) to[short,*-o] ++(0,2) node[above]{Probe}
        (mid) -- ++(3,0) coordinate(b)
        (b) node[above](B){B}

        % rx diodes
        (b) to[short,-*] ++(0,-0.5) coordinate(rx)
        (rx) -- ++(-0.5,0) to[D] ++(0,-1.5) -- ++(0.5,0)
        (rx) -- ++(0.5,0) to[D,invert] ++(0,-1.5) -- ++(-0.5,0)
        to[short,*-] ++(0,-0.5) node[ground]{}

        (b) to[short, *-o] ++(1,0)
        node[right]{Receive}
        ;
        \draw[<->] (A.east |- B.west) -- (B.west);
        \draw ($(A.east|-B.west)!0.5!(B.west)$) node[above]{\(\frac{\lambda}{4}\)};
    \end{circuitikz}
    \caption{\captiontitle{The passive switch.} Based on Diodes and \acrshort{rf} properties, the passive switch forwards the signal based on signal power. Due to the diode characteristics, the switch leaks up to \qty{0.7}{\volt} without attenuation --- including noise.}
    \labfig{passive-switch-schematic}
\end{figure}

The passive switch's working principle is based on the diode's characteristic to only start conducting above \qty{0.7}{\volt} forward bias and \acrshort{rf} wave propagation properties. When transmitting with high power, the wave amplitude is above \qty{0.7}{\volt}. Since there is no \acrshort{dc} bias the voltage also goes negative, hence the crossed diodes. They can therefore be thought of as shorts in this case so the pulse is sent from the transmit input port through point A in the centre to the probe connected at the top. Looking from point B towards ground it looks like a short-circuit as mentioned before. This short-circuit is then transformed by the \(\frac{\lambda}{4}\) length cable so it looks like an open circuit when looking from point A towards point B. Therefore the only path the transmit pulse \enquote{sees} is towards the probe, because the receive port looks like an open circuit --- there is nothing connected.

On the other hand, the received signal is very low in signal amplitude --- low enough that the diodes do not start conducting. Therefore they function as an open circuit. The signal coming from the probe port travels therefore through point A to point B and into the receiver, ignoring the paths \enquote{disconnected} by the diodes.

This switch was built by the electronic workshop and can be found in \reffig{passive-switch}. Instead of only one crossed diode pair four pairs were used. Since the wavelength of a \(f = \qty{25}{\mega\hertz}\) wave is about \(\lambda{} = \qty{12}{\metre}\), a \enquote{lumped element \(\frac{\lambda}{4}\)-impedance transformer} was used which electrically simply looks like a \qty{3}{\metre} cable. The circuit consists of an inductor in series and two shunt capacitors to its sides. To increase the attenuation of the signal the impedance transformer and diode subcircuit have been repeated three times in the realized circuit in \reffig{passive-switch}.

\begin{figure}[hbt]
    \centering
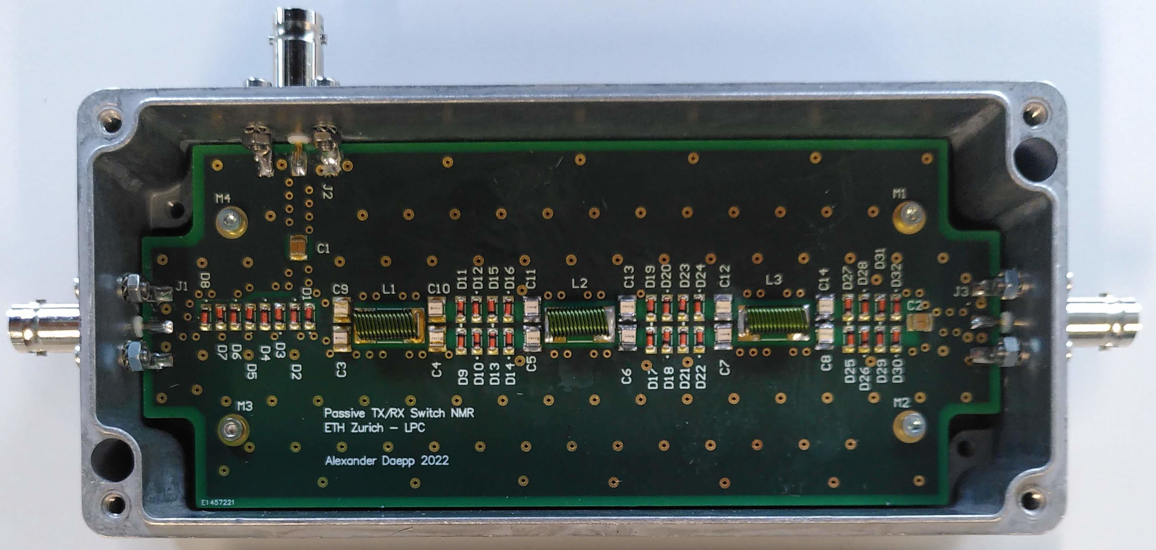
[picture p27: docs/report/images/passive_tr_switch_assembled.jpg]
    
    \caption{\captiontitle{Passive \acrshort{rf} \acrshort{tr} switch} The power amplifier output would be connected on the left, the probe at the top and the low noise amplifier on the right.}
    \labfig{passive-switch}
\end{figure}

Unfortunately, due to the diode characteristics, the switch leaked at least \qty{7}{\deci\belm} of power which would be amplified by the low noise amplifiers to levels that could damage other electronics downstream. Additionally, during receive the power amplifier would generate more noise than anticipated and the diodes would conduct lower voltages than calculated, therefore adding noise to the received signal that was orders of magnitude larger than the actual signal. For these reasons, active switch designs were explored.
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

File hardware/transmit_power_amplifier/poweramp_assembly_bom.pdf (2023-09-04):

poweramp

Page 1

Qty | Reference(s) | Value | MPN | Mouser | Notes
6 C1, C2, C3, C4, C10, C15 | | 100n/50V | C0805C104J5RACTU | 80-C0805C104J5R | 10%
2 C5, C11 | | 1u/50V | CL21B105KBFNNNG | 187-CL21B105KBFNNNG | 10%
2 C6, C12 | | 1n/50V | 08055C102KAT2A | 581-08055C102K | 10%
1 C7 | | 68p/50V | 08055A680JAT2A | 581-08055A680J
4 C8, C9, C13, C14 | | 1u/50V | CL21B105KBFNNNG | 187-CL21B105KBFNNNG | 10%
2 C16, C17 | | 10u,50V,10% | GRM21BR61H106KE43L | 81-GRM21BR61H106KE3L
2 C18, C19 | | 130p/50V | GRM2165C1H131JA01D | 81-GRM215C1H131JA01D
1 D1 | | SS13HE | SS13HE | 512-SS13HE | Schottky Diode, 30V, 1A
4 D2, D3, D4, D5 | | S1B (1N4002) | S1B-13-F | 621-S1B-F
1 F2 | | Polyfuse | 0805L075SL | | Polymeric 6V 0.75A 0.2s 40mΩ 0805 PTC
1 J1 | | Power | 68491-102HLF | 649-68491-102HLF
1 J2 | | RF_IN | 142-0701-851 | 530-142-0701-851
1 J3 | | RF_OUT | 142-0701-851 | 530-142-0701-851
1 J4 | | Power_Enable | 68491-102HLF | 649-68491-102HLF
1 L1 | | 5u6 | CC453232-5R6KL | 652-CC453232-5R6KL
1 L2 | | 470n | L-15FR47JV4E | 609-L-15FR47JV4E
1 L3 | | 360n | 36502AR36JTDG | 279-36502AR36JTDG | 5%,RF
1 Q1 | | MMBT3904 | MMBT3904-7-F | 621-MMBT3904-F
1 Q2 | | BCP51 | BCP51,115 | 771-BCP51115
2 R1, R2 | | 150 AC0805FR-07150RL | | 603-AC0805FR-07150RL
1 R3 | | 37R4 | CR0805-FX-37R4ELF | 652-CR0805FX-37R4ELF
2 R4, R7 | | 240, 1% | RC0805FR-07240RL | 603-RC0805FR-07240RL
1 R5 | | 715, 1% | RT0805FRE07715RL | 603-RT0805FRE07715RL
1 R6 | | 2k43, 1% | ERJ-6ENF2431V | 667-ERJ-6ENF2431V
2 R8, R10 | | 1k | 1623131-1 | 279-1623131-1
1 R9 | | 10k | CRCW080510K0FKEAC | 71-CRCW080510K0FKEAC
1 R11 | | 4k7 | AC0805FR-074K7L | 603-AC0805FR-074K7L
1 U1 | | ADL5536 | ADL5536ARKZ-R7 | 584-ADL5536ARKZ-R7
1 U2 | | PHA-202+ | PHA-202+ | 139-PHA-202
2 U3, U4 | | LM317_SOT-223 | LM317MQDCYR | 595-LM317MQDCYR

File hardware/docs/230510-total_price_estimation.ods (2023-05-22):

 | Description | Part-Nr. | Amount | Price per Unit | Total | Link | Comment
RX LNA Amplifier Usage Ready | Low Noise Preamplifier Evaluation Board | TB-969-13LN+ | 2 | CHF 126.00 | CHF 252.00 | https://www.minicircuits.com/WebStore/dashboard.html?model=PHA-13LN%2B
 | Low Pass Filter Evaluation Board | TB-SCLF-27+ | 2 | CHF 102.00 | CHF 204.00 | https://www.minicircuits.com/WebStore/dashboard.html?model=SCLF-27%2B
Martinos Built RX LNA Amplifier 3x | Low Noise Preamplifier | PHA-13LN+ | 3 | CHF 25.00 | CHF 75.00 | https://www.mouser.ch/ProductDetail/Mini-Circuits/PHA-13LN%2b?qs=xZ%2FP%252Ba9zWqYkwnUBoTp7PQ%3D%3D | Cheaper (11CHF) when buying > 20 pcs
 | Low Pass Filter | SCLF-27+ | 2 | CHF 12.00 | CHF 24.00 | https://www.mouser.ch/ProductDetail/Mini-Circuits/SCLF-27+?qs=xZ%2FP%252Ba9zWqbJhaqqpKrA1g%3D%3D
 | Dual Diode for Preamp Protection Circuit | BAV99 | 10 | CHF 0.23 | CHF 2.30 | https://www.mouser.ch/ProductDetail/Rectron/BAV99?qs=7pEAo90IqNFHEty9CuCrMA%3D%3D
 | General Purpose for Preamp Circuit | BAS321Z | 5 | CHF 0.17 | CHF 0.85 | https://www.mouser.com/ProductDetail/Nexperia/BAS321Z?qs=45Avz0nZxhvdAqYZS%2Fpc0w%3D%3D
 | LDO 200mA 1.4V-5.5V Power Supply | TPS7A0530PDBZR | 5 | CHF 0.71 | CHF 3.55 | https://www.mouser.com/ProductDetail/Texas-Instruments/TPS7A0530PDBZR?qs=XeJtXLiO41RzQ7iNDfPZhQ%3D%3D
 | 5.1nH Coil preamp input | LQW18AS5N1G0ZD | 5 | CHF 0.21 | CHF 1.05 | https://www.mouser.com/ProductDetail/Murata-Electronics/LQW18AS5N1G0ZD?qs=Mv7BduZupUjr7GoYEmk%252B5A%3D%3D
 | 15uH LDO Output Coil | CV201210-150K | 5 | CHF 0.09 | CHF 0.45 | https://www.mouser.com/ProductDetail/Bourns/CV201210-150K?qs=k2%252BVLg4AuuQoVlxKpSoZ1g%3D%3D
Red Pitaya Protection | Schottky Diode for RedPitaya Protection | BYS-10-25 | 10 | CHF 0.40 | CHF 4.00 | https://www.mouser.ch/ProductDetail/Vishay-General-Semiconductor/BYS10-25-E3-TR?qs=kop3EGWU%252BIusttJpdgmbLw%3D%3D
TX Power Amplifier | Power Amplifier Gain Block (32dBm) | ZHL-3A+ | 1 | CHF 290.00 | CHF 290.00 | https://www.minicircuits.com/WebStore/dashboard.html?model=ZHL-3A%2B
TX Power Amplifier Self-Built (Martinos) | Mid-Power Amplifier Evaluation Board (27.5dBm) | PHA-13HLN+ | 2 | CHF 25.00 | CHF 50.00 | https://www.mouser.ch/ProductDetail/Mini-Circuits/PHA-13HLN%2b?qs=xZ%2FP%252Ba9zWqahVjg7AJIpzg%3D%3D | Cheaper (12CHF) when buying > 20pcs
Enclosures? |  |  |  | Total | CHF 907.20
Connectors?
Caps/Resistors in E-lab?
 | TODO: Exact Parts Martinos Design (Alex probably has most of it..)

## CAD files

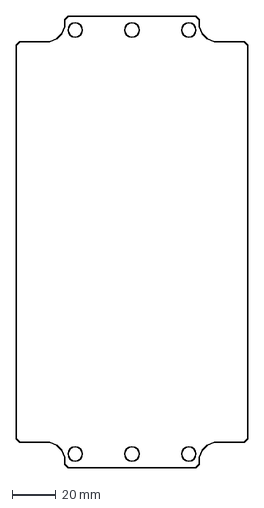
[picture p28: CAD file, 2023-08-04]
hardware/32-channel_current_source/32-channel_current_source/Hammond_1590Z150_PCB_outline.dxf
105.8 x 206.7 mm

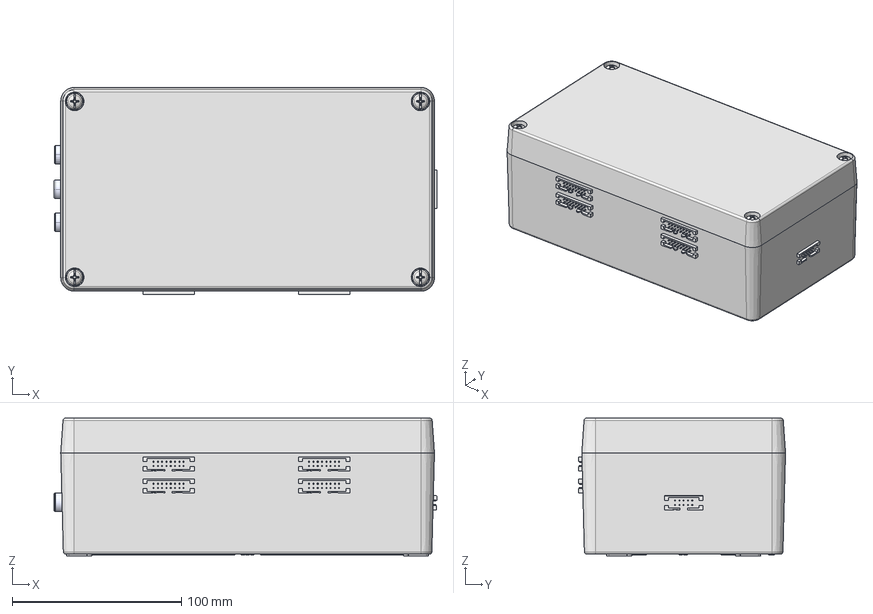
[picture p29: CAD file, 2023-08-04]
hardware/32-channel_current_source/assembly/32-channel_current_source.FCStd
226.5 x 122.5 x 81.5 mm
Pcb_85b8
R89_R_0805_2012Metric_143bbe54a2ee x 160
C6_C_0805_2012Metric_2a8ae144b11a x 72
U24_SOIC_8_39x49mm_P127mm_1dc62b96824a x 16
C3_CP_EIA_2012_15_AVX_P_d5628670eeb9 x 40
U9_SOIC_16W_75x103mm_P127mm_1b8865d83844 x 16
U1_TSSOP_20_44x65mm_P065mm_64942f3f422a x 4
J8_IDC_Header_2x08_P254mm_Vertical_SMD_1c9a4617fc0e x 4
J4_IDC_Header_2x05_P254mm_Vertical_SMD_5f2f0fe2d863
1590Z150 BOX
1590Z150 LID
1590Z150 Gasket
SC564 (screw M6-1X 35mm PN)
SC564 (screw M6-1X 35mm PN)001
SC564 (screw M6-1X 35mm PN)002
SC564 (screw M6-1X 35mm PN)003

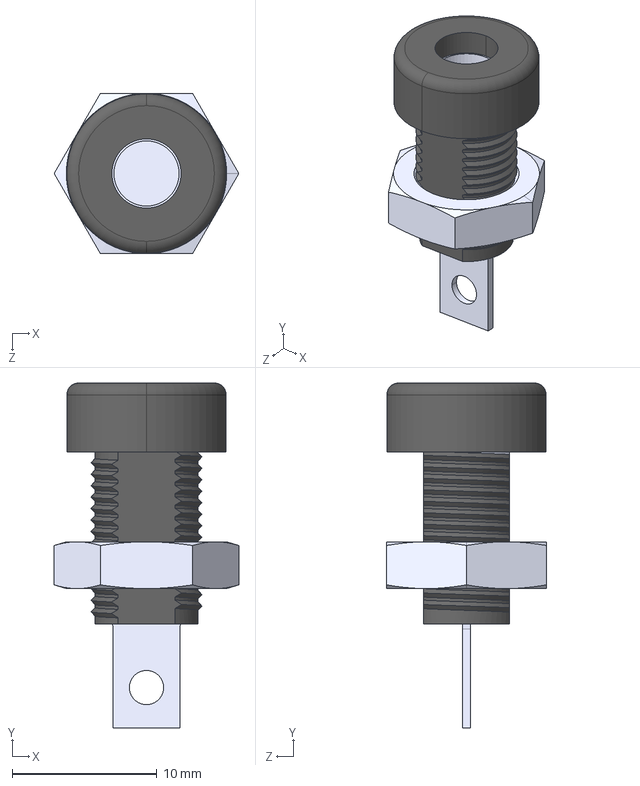
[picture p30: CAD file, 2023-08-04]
hardware/32-channel_current_source/assembly/3dmodels/keystone-PN6092.STEP
12.8 x 23.8 x 11.0 mm

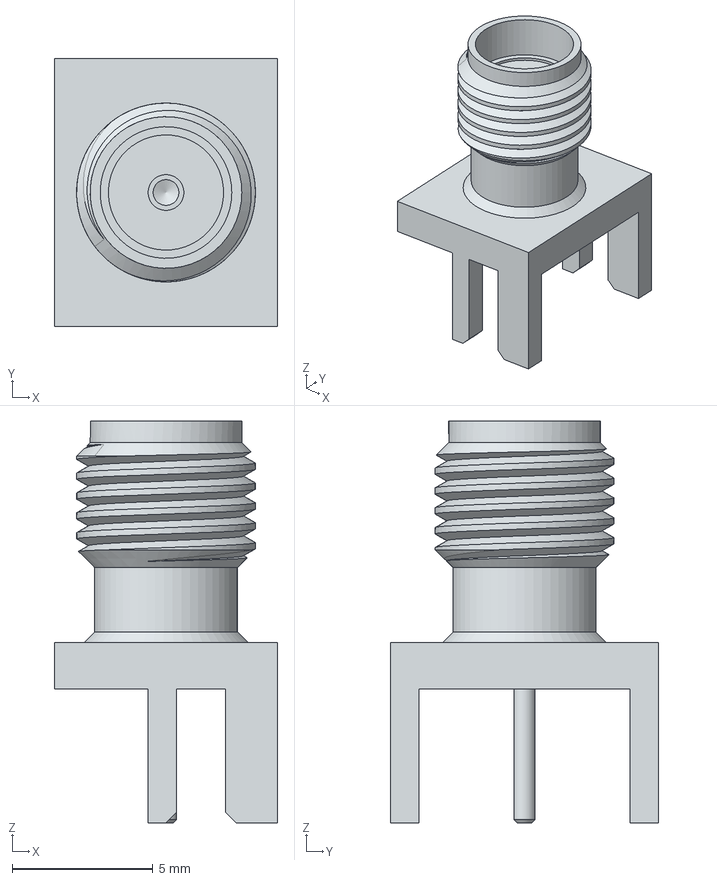
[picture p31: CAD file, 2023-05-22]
hardware/receive_preamplifier/models/142-0701-851.stp
7.92 x 9.53 x 14.3 mm

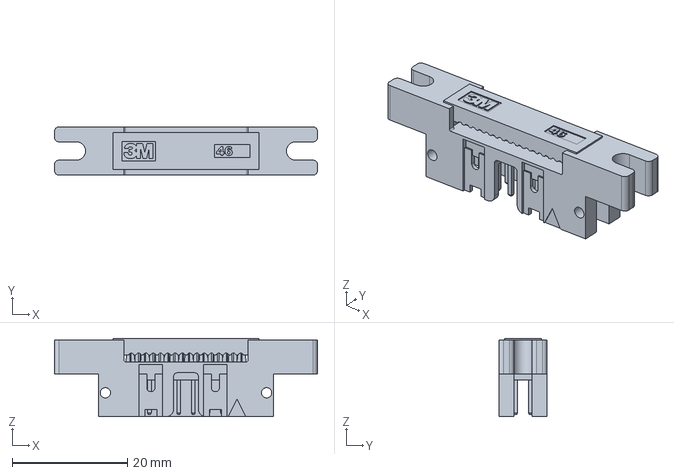
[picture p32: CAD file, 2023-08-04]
hardware/32-channel_current_source/assembly/3dmodels/4616-6000.stp
45.7 x 8.38 x 13.6 mm

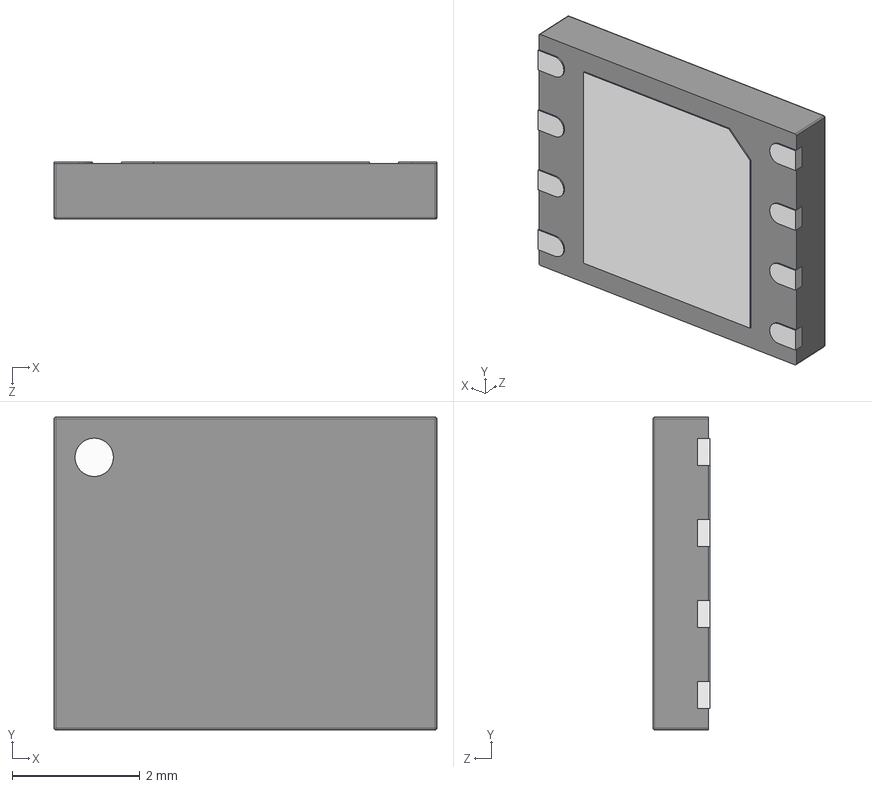
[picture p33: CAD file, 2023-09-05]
hardware/transmit_power_amplifier/models/PHA-202+.stp
6.00 x 4.90 x 0.9 mm

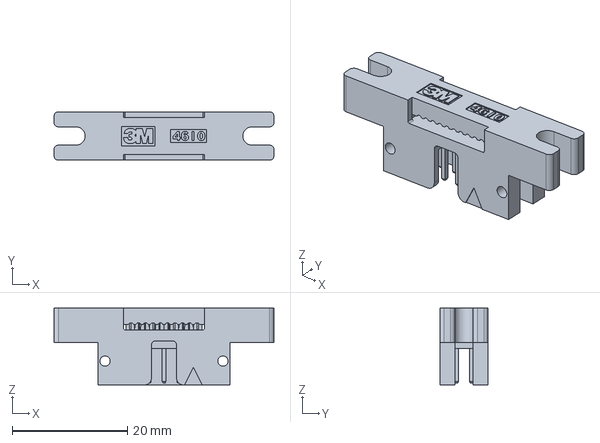
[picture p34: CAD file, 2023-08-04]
hardware/32-channel_current_source/assembly/3dmodels/4610-6050.stp
38.1 x 8.38 x 13.3 mm

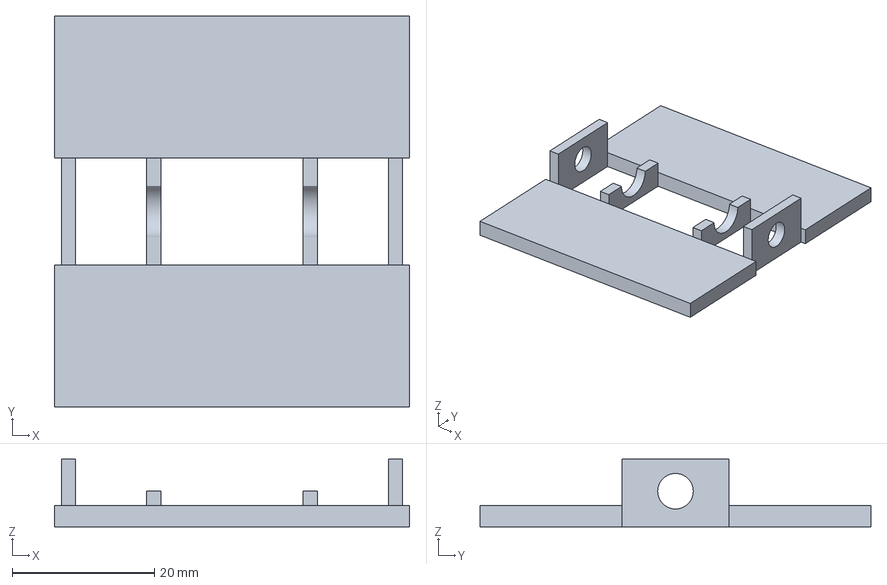
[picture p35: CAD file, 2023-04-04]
hardware/probe/andrew/230403-rf_probe_holder_innards_7-5_andrew_mcdowell.3mf
50.0 x 55.0 x 9.50 mm

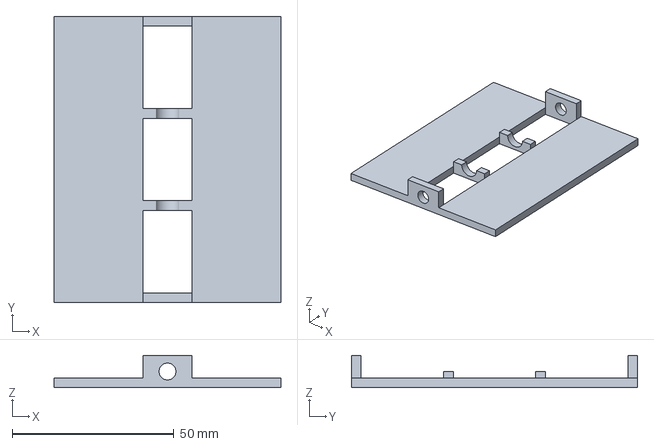
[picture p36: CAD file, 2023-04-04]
hardware/probe/probe_holder_v1/230403-probe_holder_v1.3mf
70.0 x 88.3 x 10.0 mm

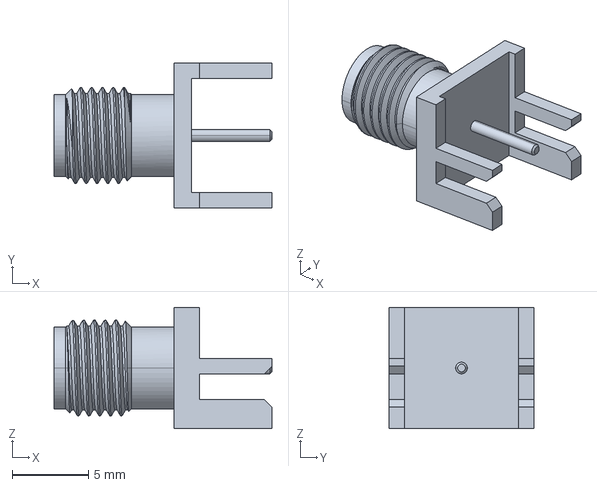
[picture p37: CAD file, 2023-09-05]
hardware/transmit_power_amplifier/models/73251-1153.stp
14.3 x 9.53 x 7.92 mm

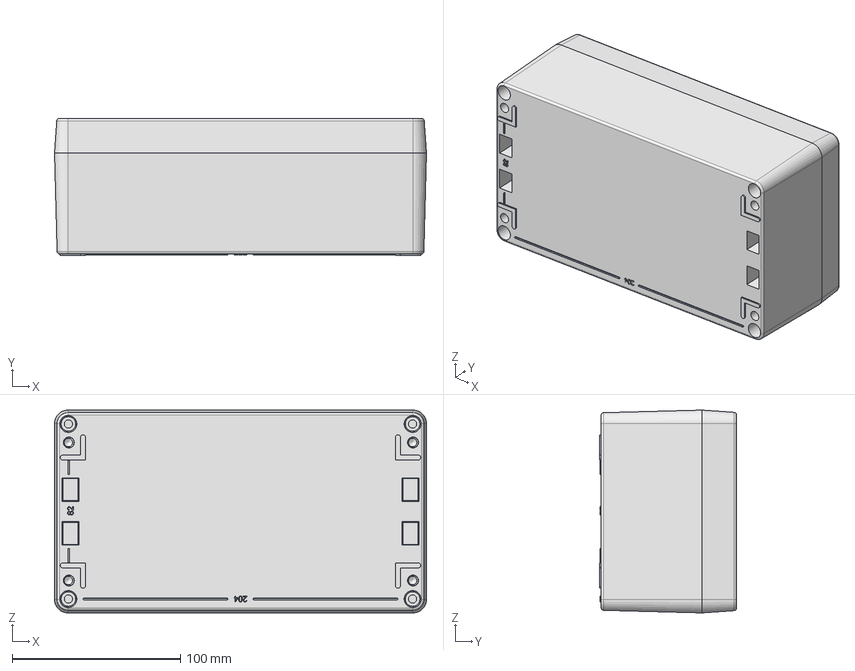
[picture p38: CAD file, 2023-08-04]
hardware/32-channel_current_source/assembly/3dmodels/1590Z150.stp
221.0 x 81.5 x 120.5 mm
1590Z150 Box
Z150LID
1590Z150 Gasket
z150-pcb
SC564 (SCREW M6X 35mm PH) x 4

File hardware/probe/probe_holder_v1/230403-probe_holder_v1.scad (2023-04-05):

// Set $fn to 20-50 for 3D printing
// Sizes in mm
$fn = 100;

// Magnet slot constants
slot_height = 10;
slot_width = 70;
slot_depth = 88.35;

// Design constants
tolerance = 0.2;
nmr_tube_diameter = 5 + tolerance;
coil_tube_diameter = 7 + tolerance;
tube_holder_width = 15;
global_thickness = 3;

// Calculated

module single_inset(width, depth, thickness)
{
    translate(v = [ -width / 2, 0, 0 ])
    {
        cube(size = [ width, depth, thickness ], center = false);
    }
}

module inset()
{
    inset_width = (slot_width - tube_holder_width) / 2;
    inset_offset = (tube_holder_width + inset_width) / 2;

    translate(v = [ inset_offset, 0, 0 ])
    {
        single_inset(width = inset_width, depth = slot_depth, thickness = global_thickness);
    }

    translate(v = [ -inset_offset, 0, 0 ])
    {
        single_inset(width = inset_width, depth = slot_depth, thickness = global_thickness);
    }
}

module tube(diameter = nmr_tube_diameter, length = global_thickness + tolerance)
{
    translate(v = [ 0, global_thickness / 2, slot_height / 2 ])
    {
        rotate(a = [ 90, 0, 0 ])
        {
            cylinder(h = length, r = diameter / 2, center = true);
        }
    }
}

module tube_holder()
{
    translate(v = [ -tube_holder_width / 2, 0, 0 ])
    {
        cube(size = [ tube_holder_width, global_thickness, slot_height ], center = false);
    }
}

module nmr_tube_holder()
{
    difference()
    {
        tube_holder();
        tube();
    }
}

module coil_tube_holder()
{
    difference()
    {
        tube_holder();
        tube(diameter = coil_tube_diameter);
        translate(v = [ -tube_holder_width / 2 - tolerance / 2, -tolerance / 2, slot_height / 2 ])
        {
            cube(size = [ tube_holder_width + tolerance, global_thickness + tolerance, slot_height + tolerance ],
                 center = false);
        }
    }
}

module holder()
{
    nmr_tube_holder();

    translate(v = [ 0, slot_depth - global_thickness, 0 ])
    {
        nmr_tube_holder();
    }

    translate(v = [ 0, (slot_depth - global_thickness) / 3, 0 ])
    {
        coil_tube_holder();
    }

    translate(v = [ 0, (slot_depth - global_thickness) / 3 * 2, 0 ])
    {
        coil_tube_holder();
    }
}

inset();
holder();

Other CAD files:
hardware/32-channel_current_source/assembly/3dmodels/keystone-PN6091.STEP
hardware/probe/andrew/230403-rf_probe_holder_innards_7-5_andrew_mcdowell.stl
hardware/probe/probe_holder_v1/230403-probe_holder_v1.stl

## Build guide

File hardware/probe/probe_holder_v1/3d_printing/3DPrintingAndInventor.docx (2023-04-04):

Inventor Parts instructions for 3D printing

Download + Configure PrusaSlicer (cable 3D printing software)

PrusaSlicer download:

- default download

upon first opening:

Original Prusa i3 MK3S & MK3S+ 0.4 und 0.8 mm nozzle

Original Prusa i3 MK3S & MK3S+ + MMUS (multimaterial) 0.4 mm nozzle

- chose Filaments Profiles Selection:

. Vendor: Extrudr

. Profile: Extrudr GreenTEC Pro Carbon *, Extrudr PETG *, Extrudr PLA NX2 *, Extrudr XPETG CF *

- Chose View mode : Expert mode

For actual print (default options should be this)

- go for 0.2 mm Quality Print setting (larger z-axis layer height -> more stability piece, may not look as nice)

- PLA default for printing

- low right printer: i3 MK3S / S+

- Print Settings -> Vertical Shells -> Perimeter -> 4 shells minimum (for any piece that needs mechanical stability.)

Print 3D part

- load .stl file (available as export from Inventor)

- Orient the part with the menu on the left for optimal printing (consider easiest printing orientation and which holes need to be modified)

- Add support where needed. Be careful about adding internal support (example to holds, usually avoid this)

- Slice part(s)

- Check by looking from top and sliding down height visible on right that all support that is needed is present AND that no parts hangs and starts from nothing (no angles >45° from vertical= z axis without support)

- get SD card from printer in machine shop, insert it into PC

- export G-code to SD card

- insert SD card into 3D printer,

- press button 3D printer for Enter, wheel to Select between prints

Make holes 3D printed

- Cut the holes of at 45° to vertical and have tangential lines coming up, forming a teardrop shaped hole -> no overhang greater than 45°. Optionally the topmost 0.5 mm of the teardrop tip can be cut away horizontally in the CAD

- chamfer all holes on both sides with 0.2 mm AFTER making the teardrop

Make a part with thread for 3D printing:

Note: Only threads with pitch min. 1 mm and at least M6 come out well. For larger than M6

From discussion with Ronny: Instruction to make threads for 3D printable piece

- Download + install CoolOrange thread modeler

- Close + reopen inventor + unblock thread Modeler

- open part with existing hole

- thread hole with thread command (under 3D Model, modify)

- Under coolOrange->threadModeler select hole and click ok

- Under 3DModel->Modify->Combine: combine thread solid and main solid (with 2 pieces, maybe more possible)

- Add phase=chamfer to thread for screw to enter AND exit: Make sketch projecting hole. Use Chamfer (0.2 mm) or use Countersink seat option with outer diameter given by phase norm for thread AND use 1 mm inner diameter to avoid affecting actual thread

3D printing, Post-processing threads

For threads that did not come out nicely (pitch <1 mm or size < M6) need to be drilled afterwards.

- get taps (Gewindebohrer) of proper size + pitch with hand drill.

Bosch Drill in machine shop: Arrows on left and right side of drill change drilling forward <-> backward.

- Load tap by holding front of drill and drilling in one direction or rotating front of drill, both reduce / increase tap holding the chuck (Gewindefutter)

- Hold the tap perpendicular to the hole and drill the tap through.

- If the inner diameter of the threaded part is larger than the shaft (end part) of the tap, then drill all the way through, remove the tap from the drill and pull the tap out through the hole. Otherwise drill through, remove all the plastic that was drilled off, reverse drilling direction and drill the tap back out again. (If the plastic trash if not removed, it can destroy the thread on the way back out)

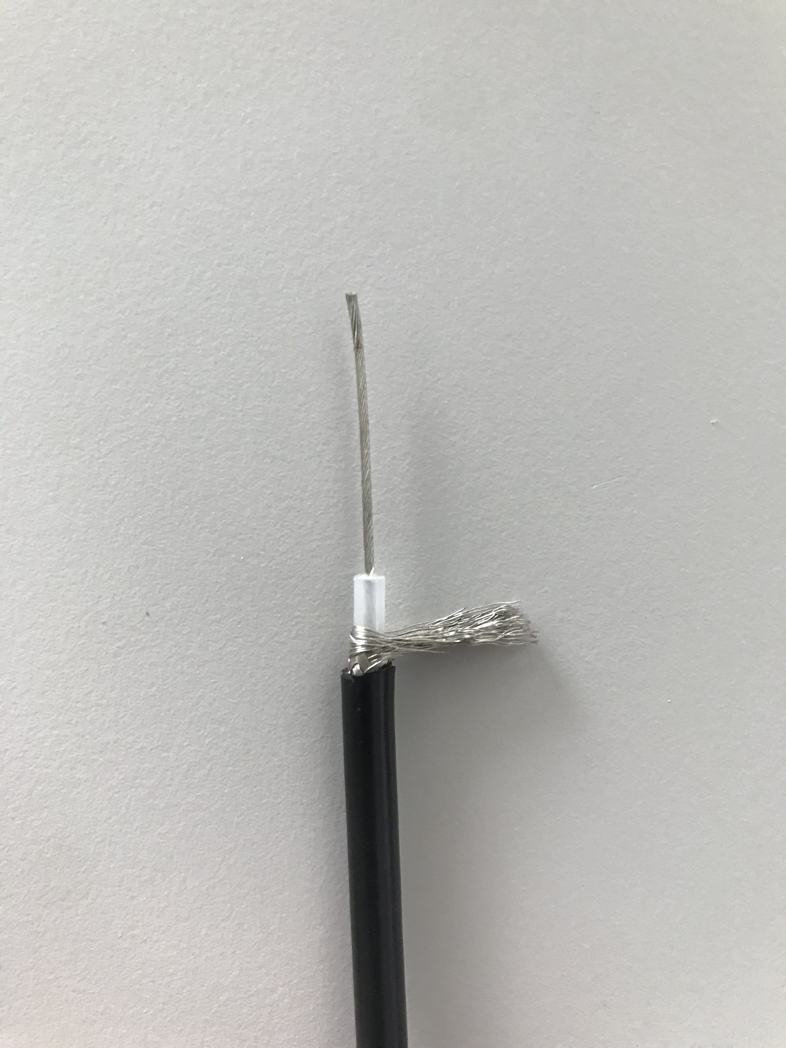
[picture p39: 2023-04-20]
hardware/probe/probe_holder_v1/pictures/230418-coax_before_soldering.JPG

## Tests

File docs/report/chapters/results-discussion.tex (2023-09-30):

\setchapterpreamble[u]{%
    \margintoc\hfil%
    \dictum[Willy Brandt]{Es wächst zusammen,\\was zusammengehört.}
}
\chapter{The complete spectrometer}
\labch{complete}

The following sections look at the built spectrometer from a user's point of view. The first \refsec{user-perspective} describes the assembly and operation of the spectrometer built above. The following sections set up the console (\refsec{console-setup}) and control software (\refsec{control-software}). Lastly, \refsec{measurement} discusses the how to measure a signal with a simple and approachable example.

\section{Software Setup}
\labsec{user-perspective}
\begin{marginfigure}
    \includesvg{images/logo_magnETHical.svg}
    \caption{Logo of the \magnethical{} spectrometer project}
    \labfig{logo-magnethical}
\end{marginfigure}

The spectrometer was designed with ease of use and reconfigurability in mind. The individual parts are placed on separate boards, connected with standard \acrshort{sma} connectors. Broken parts can thus be easily exchanged. Old already existing parts can be used in conjunction with newly developed ones, facilitating the re-use of hardware and ensuring operation while a broken part is fixed or upgraded.

The software -- while still incomplete -- has the same goals as the hardware. It is written in \gls{python} with extensive documentation, comments throughout the code and accompanying guides to get started\sidenote{Take a look at the official \lstinline{README.md} in the \href{https://github.com/M4a1x/nmr-spectrometer/tree/master/software/spectrometer}{official repository}}. Generally, the code tries to adhere to the ideas presented in \enquote{Uncle Bob's} book \textit{Clean Code} \sidecite{martinCleanCodeHandbook2008}.

There are five main parts to the spectrometer as explained in \nrefch{methods}:
\begin{description}
    \item[The console] (i.e. the RedPitaya) responsible for sending, receiving and processing the \acrshort{rf} signals.
    \item[The power amplifiers] responsible for amplifying the signal generated by the console
    \item[The transmit-receive switch] responsible for switching between sending a signal into the probe from the transmit channel and receiving a signal back from the probe into the receive channel
    \item[The probe] consisting of the probe holder and the probe coil, responsible for emitting and receiving the \acrshort{rf} signal
    \item[The \acrlong{lna}s] responsible for amplifying the weak signal received by the probe before feeding it to the console for processing
\end{description}
The short conceptual overview is reproduced in figure \reffig{overview} for the reader's convenience. Each output needs to be connected to the input of the next device. The power connections are not shown in favour of clarity, but each part is labelled with the possible input voltages, in a range of \qtyrange{7}{15}{\volt}. For a more detailed description of the individual parts and their connections see the \magnethical{} project page (compare \reffig{logo-magnethical}) or the descriptions above.

\begin{figure*}[!htb]
    \centering
    \begin{circuitikz}[european]
        \ctikzset{bipoles/amp/width=0.9}
        \draw[nodes={align=center}]
        (0,0) coordinate(mid)

        % RP
        (mid) node[draw, align=center, minimum height=5.5cm, minimum width=2cm](redpitaya){Red\\Pitaya\\SDRlab\\122-16}
        ($(redpitaya.east)!0.75!(redpitaya.north east)$) coordinate(rptx) node[left]{TX\\(Out 1)}
        ($(redpitaya.east)!0.75!(redpitaya.south east)$) coordinate(rprx) node[left]{RX\\(In 1)}

        % TX
        (rptx) to[lowpass,l=SCLF-27+,>] ++(5,0)
        to[amp,t=\acrshort{pa},l=ADL5536\\PHA-202+,>] ++(5,0) coordinate(tx)

        % Circulator
        (mid -| tx) node[circulator,label={left:QPC6324}](circ){}
        (tx) -| (circ.n) node[inputarrow,rotate=270]{}

        % RX
        (rprx -| circ) coordinate(rx)
        (circ.s) |- (rx)
        (rx) to[amp,t=\acrshort{lna},l=PHA-13LN+,>] ++(-2.5,0)
        to[amp,t=\acrshort{lna},l=PHA-13LN+,>] ++(-2.5,0)
        to[amp,t=\acrshort{lna},l=PHA-13LN+,>] ++(-2.5,0)
        to[lowpass,l=SCLF-27+,>] ++(-2.5,0) node[inputarrow,rotate=180]{}

        % Probe
        (circ.e) -- ++(1,0)
        node[dinantenna](probe){}
        node[below=1ex]{3D-printed\\probe holder}
        ;
    \end{circuitikz}

    \caption{\captiontitle{Component overview.} The schematic contains all physical parts of the \acrshort{nmr} spectrometer that need to be connected through \acrshort{sma} cables.}
    \labfig{overview}
\end{figure*}

\section{Setting up the RedPitaya}
\labsec{console-setup}
Having ordered or built the parts\sidenote{Again, see \refch{methods}}, connected them using \acrshort{sma} cables and powered them through a lab power supply, the console needs to be configured. The configuration of the console is relatively simple as most of the complexity has been programmed into the \gls{python} control library. The user thus only needs to ensure that a working \acrshort{linux} distribution is running on the \acrshort{rp} and that the \acrshort{ip} address is known. The official distribution that is pre-installed on the micro SD card that ships with the \acrshort{rp} is completely sufficient.

If the user needs to create a new microSD card, the \href{https://redpitaya.readthedocs.io/en/latest/quickStart/SDcard/SDcard.html}{setup of the microSD card is described in the \acrshort{rp} docs} and is summarized here for simplicity on a Linux based system.

\begin{enumerate}
    \item \href{https://redpitaya.readthedocs.io/en/latest/quickStart/SDcard/SDcard.html}{Download the newest microSD card image}
    \item Insert the microSD card into your computer.
    \item Determine its name using \lstinline{lsblk} or \lstinline{df -h}, e.g. \lstinline{/dev/mmcblk0} or \lstinline{/dev/sdc}.
    \item Copy the image on the microSD card using\\ \lstinline{dd bs=1M if=red_pitaya_image_file.img of=/dev/mmcblk0 status=progress}
    \item Done!
\end{enumerate}

The \acrshort{rp} needs to be reachable through Ethernet from the computer running the control software. The easiest way is to connect them both to a \acrshort{dhcp} server\sidenote{An example for a \acrshort{dhcp} server would be any router or WiFi access point that automatically provides you internet access.} in the same network and lookup the IP address it got assigned by entering the name printed on it into a web browser. For a manual setup method for a direct connection in an isolated lab environment, see the \lstinline{README.md} in the control software repository or the \href{https://redpitaya.readthedocs.io/en/latest/quickStart/connect/connect.html#static-ip-configuration}{Static IP configuration guide in the RedPitaya documentation}\sidenote{For this document we assume the RedPitaya is reachable on the \acrshort{ip} \lstinline{192.168.1.100}}.

The control software needs to be able to remotely log in to the system through \acrfull{ssh}. For this, the \lstinline{sshd} server needs to be running, which is the case for almost any image you find -- including the official RedPitaya image\sidenote{The default username is \lstinline{root} and the default password is also \lstinline{root}. Sometimes there is no password -- in that case, just press \enquote{Enter} when asked for one. Remember nothing -- not even stars -- is displayed when typing the password}.

It is highly recommended to set up a passwordless login scheme from the computer to the \acrshort{rp}. Listing \ref{lst:pubkey} presents the necessary commands for creating a \lstinline{keyfile} and copying it to the \acrshort{rp} on a \acrshort{linux} machine. When asked, accept the recommended settings for the \lstinline{keyfile} -- do not set a password for it! Enter your password when prompted to do so.

\begin{listing}[h!bt]
    \begin{minted}{shell-session}
        $ ssh-keygen -t ed25519             # create a keyfile
        $ ssh-copy-id root@rp-xxxxxx.local  # alternatively: root@192.168.1.100
    \end{minted}
    \caption{\captiontitle{Generating SSH keyfiles for passwordless login.} Accept default configurations when prompted.}
    \label{lst:pubkey}
\end{listing}

\section{Setting up the control software}
\labsec{control-software}
On the computer, you need \href{https://git-scm.com/}{\lstinline{git}} and \href{https://www.python.org/}{\lstinline{python3}} to run the software. On Linux, they can usually be installed with one of the commands in Listing \ref{lst:install-prerequisites}.

\begin{listing}[h!bt]
    \begin{minted}{shell-session}
        $ dnf install python3 git   # (Fedora/RHEL/CentOS/...)
        $ apt install python3 git   # (Debian/Ubuntu/Mint/...)
        $ pacman -S python git      # (Arch/Manjaro/Artix/...)
    \end{minted}
    \caption{Installing prerequisites}
    \label{lst:install-prerequisites}
\end{listing}

With the prerequisites installed, the user can now install the spectrometer control software \gls{python} package. However, it is generally recommended to use \enquote{virtual environments}\sidenote{For more details see \href{https://peps.python.org/pep-0668/}{PEP 668} and \href{https://peps.python.org/pep-0405/}{PEP 405}} that create a new environment with packages and executables separate from the system and other programs. This functionality is already included in \gls{python}. Listing \ref{lst:setup} describes how to set up and activate a new \enquote{virtual environment} inside a \lstinline{~/spectrometer} folder.

\begin{listing}[h!bt]
    \begin{minted}{shell-session}
        $ cd ~
        $ mkdir spectrometer
        $ cd spectrometer
        $ python3 -m venv .venv
        $ source .venv/bin/activate    # Linux
        $ .venv/bin/activate.ps1       # Windows Powershell
        $ .venv/bin/activate.bat       # Windows Cmd
    \end{minted}
    \caption{Set up of a \enquote{virtual environment} (often called \enquote{venv}) in \gls{python}}
    \label{lst:setup}
\end{listing}

The user can now install the control software including all dependencies independently from the system they are working on using the commands in Listing \ref{lst:install}. The second one might take a while to run.

\begin{listing}[h!bt]
    \begin{minted}{shell-session}
        $ git clone https://github.com/M4a1x/nmr-spectrometer.git
        $ python3 -m pip install ./nmr-spectrometer/software/spectrometer
    \end{minted}
    \caption{Installation of the python library with automated dependency resolution using \href{https://pypi.org/project/pip/}{\acrshort{pip}}. Assuming the user already installed and activated a virtual environment as described in Listing~\ref{lst:setup}.}
    \label{lst:install}
\end{listing}

The installation process automatically adds scripts for controlling the spectrometer to the command line seen in Listing \ref{lst:cmds}. These can be used to manually flash the firmware, set up the spectrometer hardware, and start the sequence processing server.

\begin{listing}[h!bt]
    \begin{minted}{shell-session}
        $ magnethical flash_fpga
        $ magnethical setup
        $ magnethical start
        $ magnethical stop
        $ magnethical is_running
    \end{minted}
    \caption{Command line spectrometer control commands}
    \label{lst:cmds}
\end{listing}

\section{Performing a Measurement}
\labsec{measurement}
With the package and all dependencies installed as described above, the system is ready to be used. The software and hardware support arbitrary pulse sequences with one transmit and one receive channel\sidenote{This could be expanded software side to 2 receive and 2 transmit channels}. A simple example is described here, for a more in-depth explanation of all the different functions, please look at the \acrshort{api} reference in the repository. More examples for measurements are available as well --- in particular, all measurements described below in \refch{results} are located in the \lstinline{scripts} folder inside the Python package as well as a full demo notebook\sidenote{To be precise: a \href{https://jupyter.org/}{Jupyter Notebook}. It is a tool for integrating Python code with text blocks and inline outputs making data analysis and plotting more convenient.} inside the \lstinline{docs} folder.

\begin{listing}[h!bt]
    \begin{minted}{python}
        # Import the necessary packages
        from spectrometer import (
            Server,
            ConnectionSettings,
            Spectrometer,
            NMRSequence,
            FID1D
        )

        # Connect the server platform (i.e. the RedPitaya)
        server = Server("192.168.1.100")

        # Flash the FPGA bitstream (or "low level server")
        server.flash_fpga()

        # Compile the server on the spectrometer (or "high level server")
        server.setup()

        # Start the server on the spectrometer
        server.start()

        # Setup the spectrometer connection
        connection_settings = ConnectionSettings(ip_address="192.168.1.100")

        # Create the spectrometer object
        spectrometer = Spectrometer(
            tx_freq=25_091_000,  # Center transmission frequency
            rx_freq=None,  # Receive frequency
            sample_rate=320_000,  # samples/second
            server_config=connection_settings,
        )

        # Connect to the spectrometer server
        spectrometer.connect()

        # Define and send the sequence
        seq_simple = NMRSequence.simple(pulse_length_us=9, delay_us=25, record_length_us=20_000)
        data = spectrometer.send_sequence(seq_simple, debug=True)

        # Save
        fid = FID1D(
            data=data,
            spectral_width=spectrometer.sample_rate,
            carrier_freq=0.0,
            observation_freq=spectrometer.rx_freq,
            label="1H",
            sample="Water",
            pulse="single_90_degree_pulse,length=9us,delay=30us",
            spectrometer="magnETHical v1.0",
        )
        fid.to_file("my_experiment.fid")

        # Plot, e.g.
        fig = fid.plot()

        # Spectrum
        spectrum = fid.spectrum()  # zero-fill, FFT, zero-order phase correction
        fig = spectrum.hz.plot()
        fig = spectrum.ppm.plot()
        fit_spectrum, fitpeaks = spectrum.hz.fit()
        peaks = spectrum.hz.peaks()
    \end{minted}
    \caption{\captiontitle{Performing a measurement on a sample using the control software}. The hardware is assumed to be set up, connected and powered up. The \qty{5}{\milli\metre} NMR tube with the sample should be inside the probe holder that was inserted into the magnet and the connection between the RedPitaya and the Laptop running the control software was verified. The code sends a single pulse of \qty{9}{\micro\second}, waits for \qty{25}{\micro\second}, records the received signal and plots it in the time and frequency domains.}
    \label{lst:demo}
\end{listing}

\section{Editing the control software}
The source code of the control software can be easily obtained through \lstinline{git} as done in line 2 of Listing \ref{lst:hatch}. It uses \lstinline{hatch} for package and dependency management, which needs to be installed globally. \lstinline{hatch} then provides commands for running a demo Jupyter notebook, unittests\sidenote{unittests are individual tests of separate components as opposed to integration tests that verify the interplay and compatibility of several units}, compiling and reading the documentation. The demo does not work offline and needs a connection the spectrometer. The documentation and unittests are standalone. See Listing \ref{lst:hatch} for examples on using the commands.

\begin{listing}[h!bt]
    \begin{minted}{shell-session}
        $ python -m pip install hatch  # Install globally with no venv activated
        $ git clone https://github.com/M4a1x/nmr-spectrometer.git
        $ cd nmr-spectrometer
        $ hatch run demo  # Open the demo Jupyter notebook in a browser
        $ hatch run docs  # Compile and open the documentation and API reference
        $ hatch run test  # Run the unit tests
        $ hatch shell     # Activate the virtual environment
    \end{minted}
    \caption{\captiontitle{Using hatch to perform common tasks when editing the control software}. The invoked commands can be found in the \lstinline{pyprojects.toml} file in the repository. Examples for using the library are available in the \lstinline{scripts} and \lstinline{docs} folders.}
    \label{lst:hatch}
\end{listing}

\setchapterpreamble[u]{%
    \margintoc\hfil%
    \dictum[Wethern's Law]{Assumption is the mother\\of all fuckups.}
}
\chapter{Experimental Results}
\labch{results}
The following presents the measurement results of different pulse sequences sent with the spectrometer and analysed with the control software. The code used to obtain these exact measurements can be found in the repository inside the \lstinline{scripts} folder, and the raw data inside the \lstinline{data} folder.

\section{Measuring a water signal}
\labsec{water-signal}

\begin{marginfigure}
    \centering
    \includesvg{simple_pulse_sequence.svg}
    \caption{\captiontitle{Simple pulse sequence} The usual depiction of a simple pulse sequence. The \enquote{RF pulse} is a high frequency \acrshort{rf} pulse close to the resonance frequency of the nuclei to be observed. After the pulse, a decaying cosine signal can be received on the same coil -  the so-called \acrfull{fid}.}
    \labfig{simple-pulse-sequence}
\end{marginfigure}

Probably the simplest \acrshort{nmr} pulse sequence consists of a single \(\frac{\pi}{2}\)-excitation pulse as seen in \reffig{simple-pulse-sequence}. Inserting a standard \qty{5}{\milli\metre} \acrshort{nmr} tube filled with water with the probe holder inside the magnet, an experiment can be performed using the commands described in \refsec{measurement}. Before the experiment, the \(\frac{\pi}{2}\)-pulse length has manually been determined to be \qty{8}{\micro\second} by varying the pulse length, finding the length of a \(\pi\) pulse and confirming that a pulse of half the duration gives a maximum signal. The coil rings less than \qty{25}{\micro\second}, confirmed by looking at the received signal through an oscilloscope. \reffig{fid-raw} shows the real part of the received signal from a water probe after the coil ringing.

\begin{figure}[h!bt]
    \centering
    
    \caption{\captiontitle{\acrfull{fid} of water.} The signal was recorded after a \qty{8}{\micro\second} impulse of a strength of \qty{1}{\watt} and a delay of \qty{25}{\micro\second}, waiting for the coil to ring down. \enquote{Andrew's probe} was used in this measurement with a transmit frequency of \qty{25.09}{\mega\hertz}}
    \labfig{fid-raw}
\end{figure}

\reffig{fid-raw} shows a nice exponentially decaying sine wave. There are some points at the beginning of the signal that clearly do not fit in this model. They can be explained through the impulse response of the discrete \acrshort{cic} filters and should ideally be discarded. Nevertheless, \reffig{fid-sine-fit} shows a least squares optimized fit of a decaying exponential sinusoid. Despite the outliers in the beginning this works quite well and confirms the first impression.

\begin{figure}[h!bt]
    \centering
    
    \caption{\captiontitle{\acrfull{fid} of water with a sine fit.} The blue data is the same as in \reffig{fid-raw}. The orange dashed line is the result of a least squares fit of a decaying sine wave. It shows an exponential decay in amplitude with a $T_2^*$ of \qty{2.5}{\milli\second} and a dominant frequency of about \qty{590}{\hertz}}
    \labfig{fid-sine-fit}
\end{figure}

The decay constant \(T_2^*\) of \qty{2.5}{\milli\second} is relatively short. In a properly shimmed high-field spectrometer it would be expected to be a few seconds --- several orders of magnitude higher. The discrepancy can easily be explained by the lack of any active shimming. Therefore, a slightly different magnetic field acts on the individual water molecules, causing them to have slightly different resonance frequencies. As a result, they will de-phase quickly.

The Fourier spectrum in \reffig{fft-raw} was obtained through zero-filling the data, a complex discrete Fourier transform and an automatic zero order phase shift. As expected we obtain a single peak stemming from the two magnetically identical \ch{^1H} in water, whose chemical structure is shown in \reffig{h2o}.

\begin{marginfigure}
    \centering
    \includesvg{h2o.svg}
    \caption{\captiontitle{Structure of \ch{H_2O}.} Observe the two \ch{H} atoms that should result in an identical NMR signal.}
    \labfig{h2o}
\end{marginfigure}

The shape seems almost Lorentzian, except for two deviations: %
\begin{enumerate*}[label=(\arabic*)]
    \item The (here small) broadening on the right side, which could be explained by the lack of active shimming and
    \item the baseline distortion around the peak, which can be explained through the first erroneous points in the \acrshort{fid} and the window effect of cutting off the signal in the beginning and end.
\end{enumerate*}%
\sidenote{See for example the right side of \reffig{rect} in the concepts chapter. Remember, that figure shows the absolute amplitude, not the real part}
The shimming error could be a \(Z^2\) shimming error, see \sidecite{minerShimmingAinMagic1997} for examples of different kinds of shimming errors and their influences on the spectrum.

\begin{figure}[h!bt]
    \centering
    
    \caption{\captiontitle{Fourier spectrum of \reffig{fid-raw}.} It shows a Lorentz-shaped peak around roughly \qty{600}{\hertz} with a slight broadening on the right side and a distorted baseline. The data was obtained through an automatic zero fill, complex Fourier transformed and automatically zero order phase corrected with a shift of \ang{37}.}
    \labfig{fft-raw}
\end{figure}

Performing a least-squares fit again the two deviations become even more apparent as seen in \reffig{fft-fit}. Even without shimming the linewidth is relatively narrow with a full width at half maximum of \qty{118}{\hertz} or about \qty{4.7}{ppm}.

The Fourier spectrum can be used to easily estimate the \acrfull{snr} of the signal. With only one peak this is especially easy. The noise is estimated by calculating the standard deviation under the assumption that the expected value \(\mu{}\) is \(0\), which works by modelling it as a sum of \acrfull{iid} random variables or more specifically \acrfull{gwn}\sidenote{Due to the central limit theorem for large \(n\)}.
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

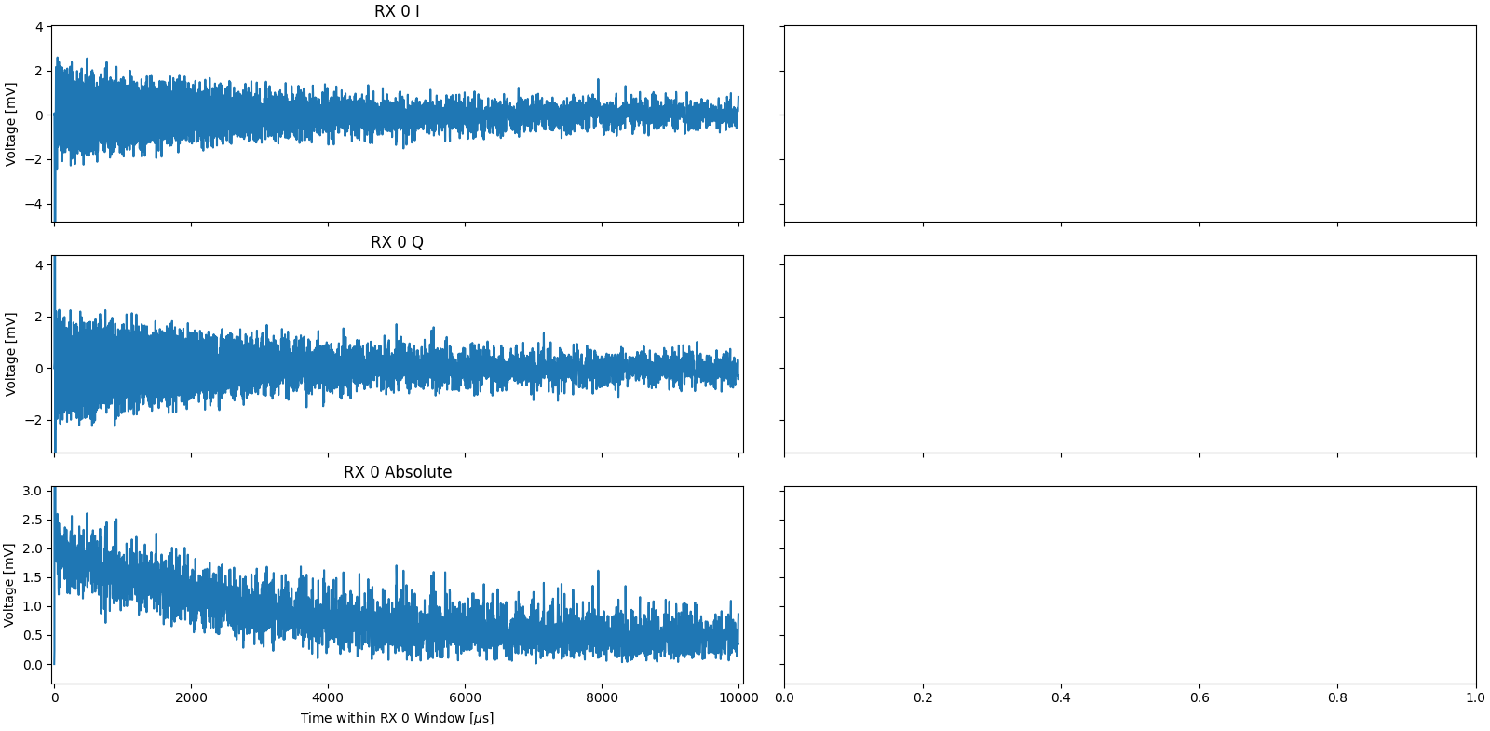
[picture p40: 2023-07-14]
docs/measurements/230714-andrew_probe_water_sample_3lna_5us_pulse_10ms_aq.png

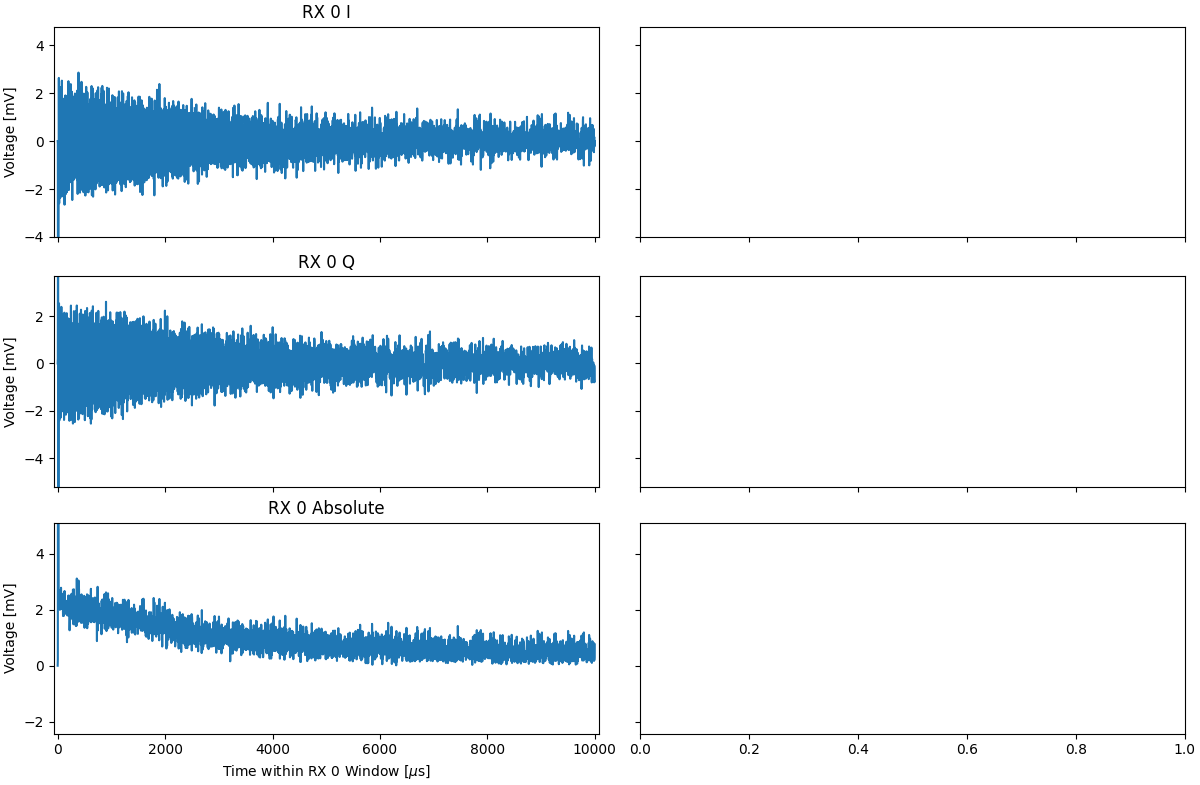
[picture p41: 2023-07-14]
docs/measurements/230714-andrew_probe_water_sample_3lna_7.5us_pulse_10ms_aq.png

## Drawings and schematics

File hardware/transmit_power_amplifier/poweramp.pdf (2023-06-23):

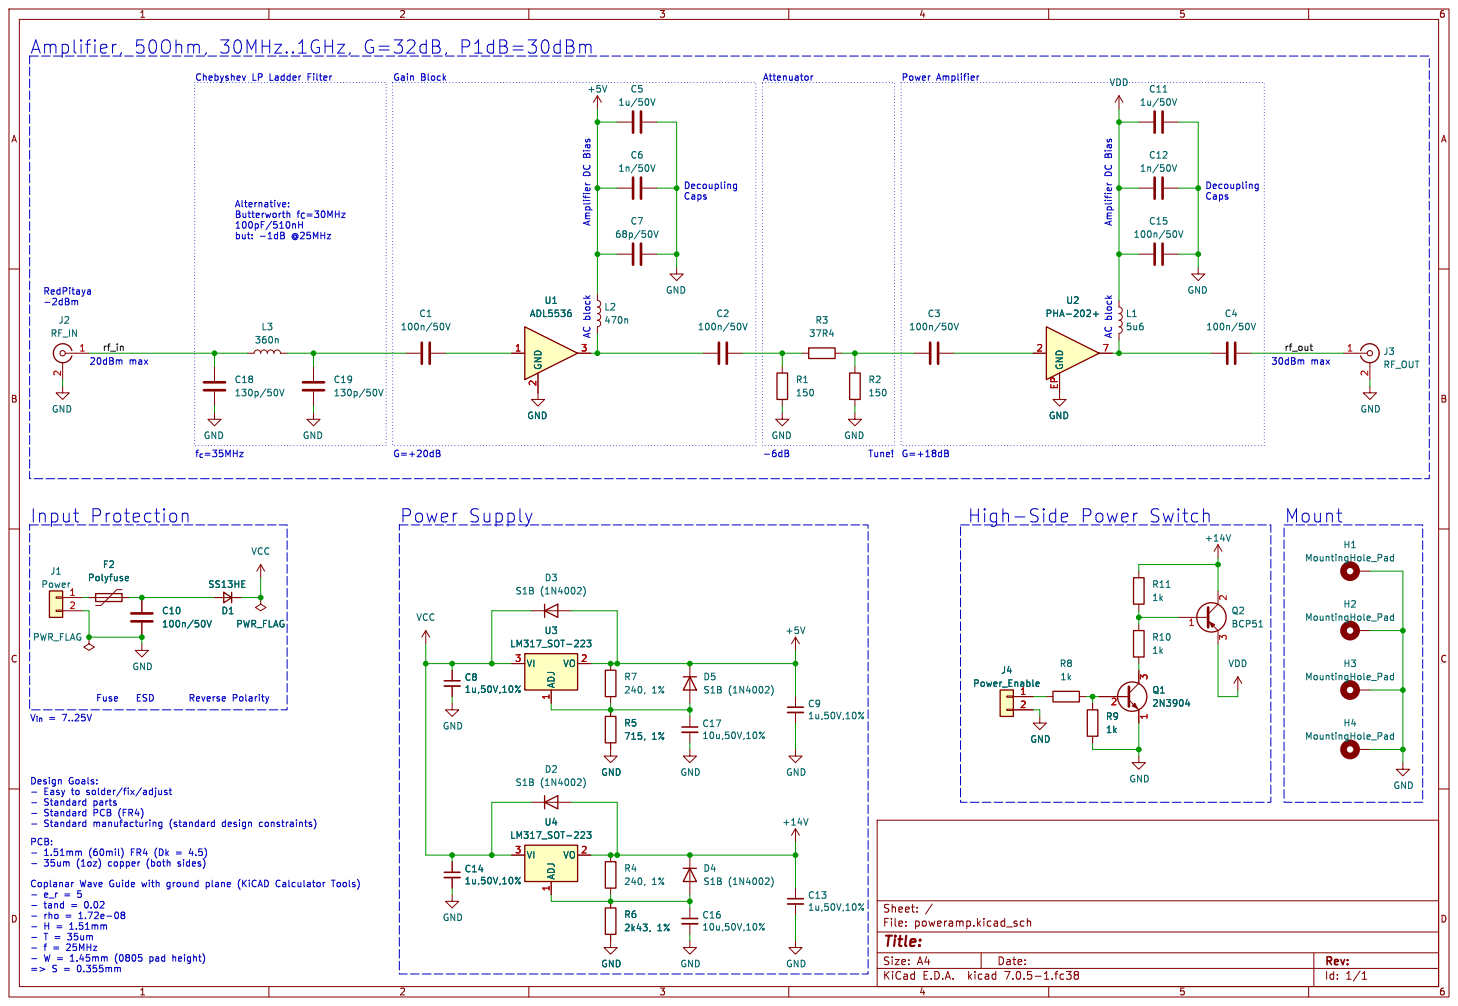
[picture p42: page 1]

Chebyshev LP Ladder Filter RedPitaya

Design Goals: - Easy to solder/fix/adjust - Standard parts

Id: 1/1 Title: File: poweramp.kicad_sch Sheet: /

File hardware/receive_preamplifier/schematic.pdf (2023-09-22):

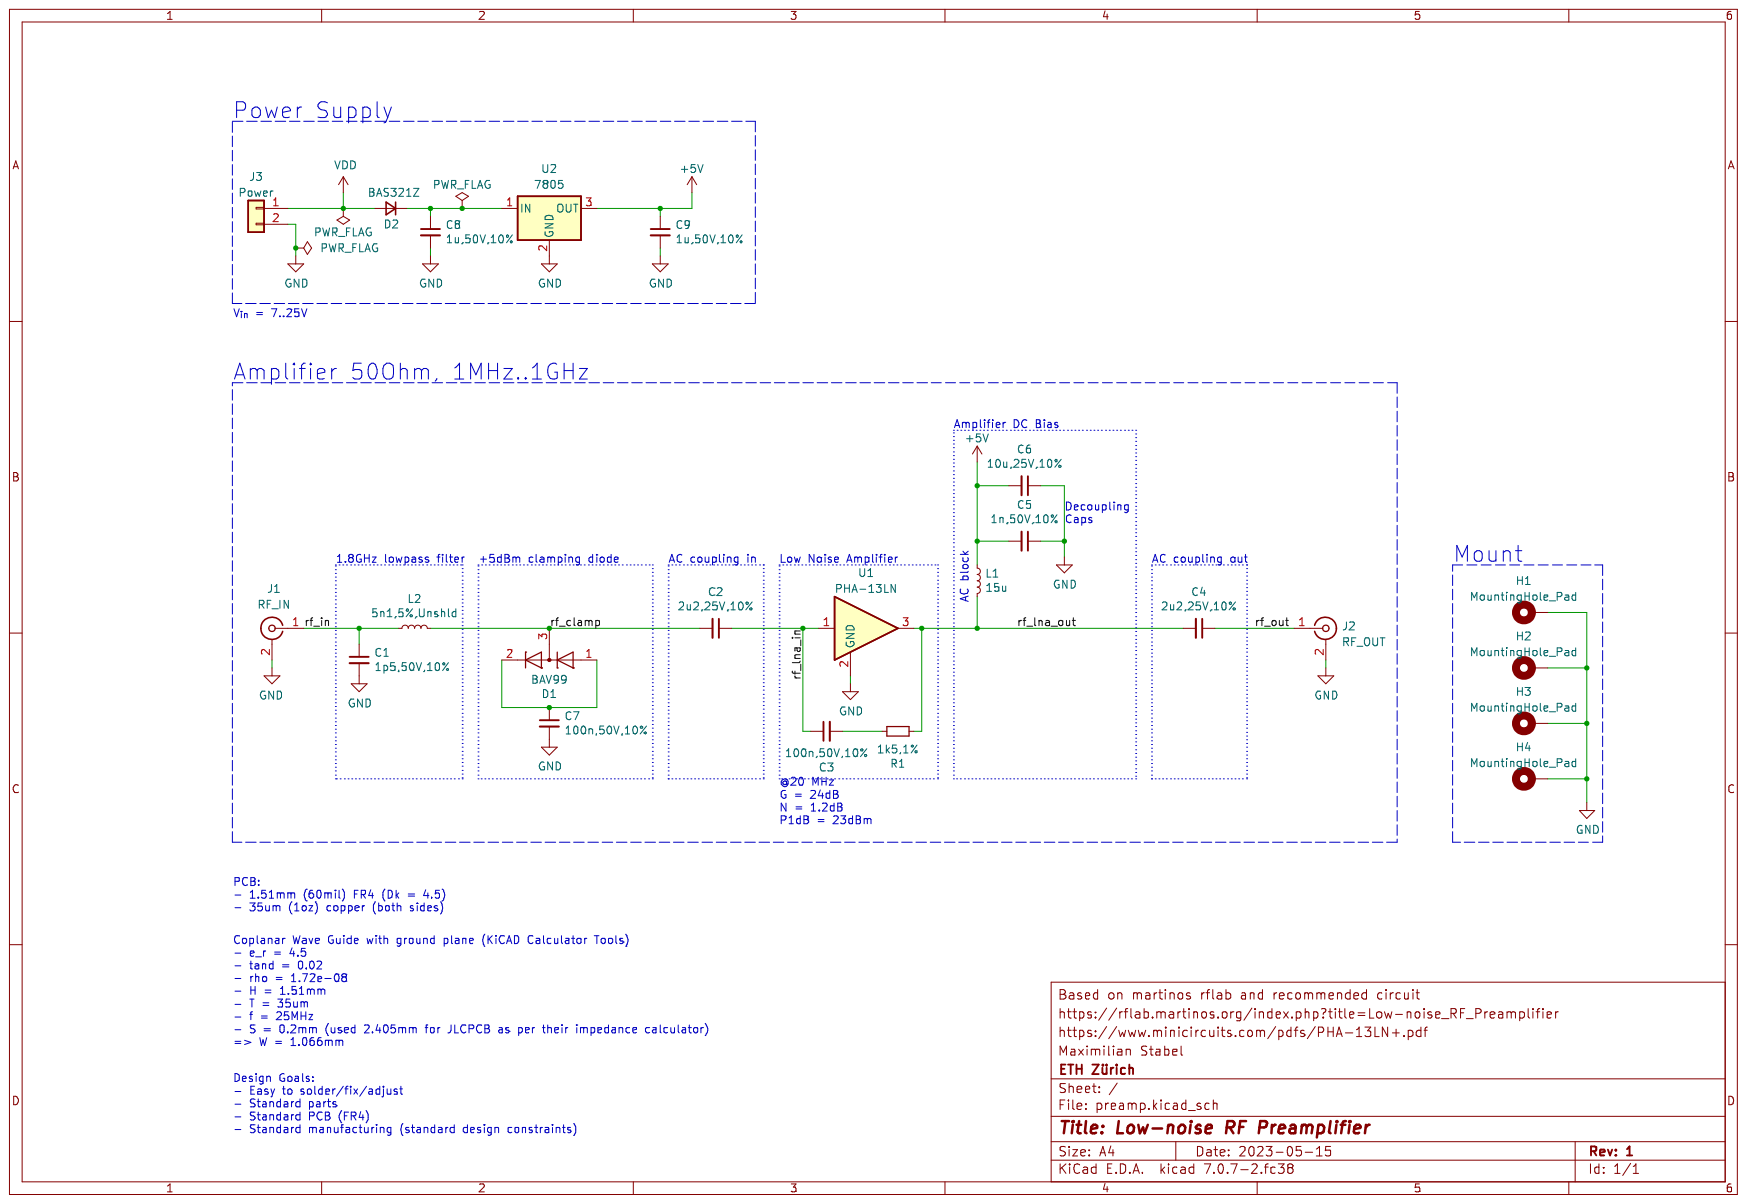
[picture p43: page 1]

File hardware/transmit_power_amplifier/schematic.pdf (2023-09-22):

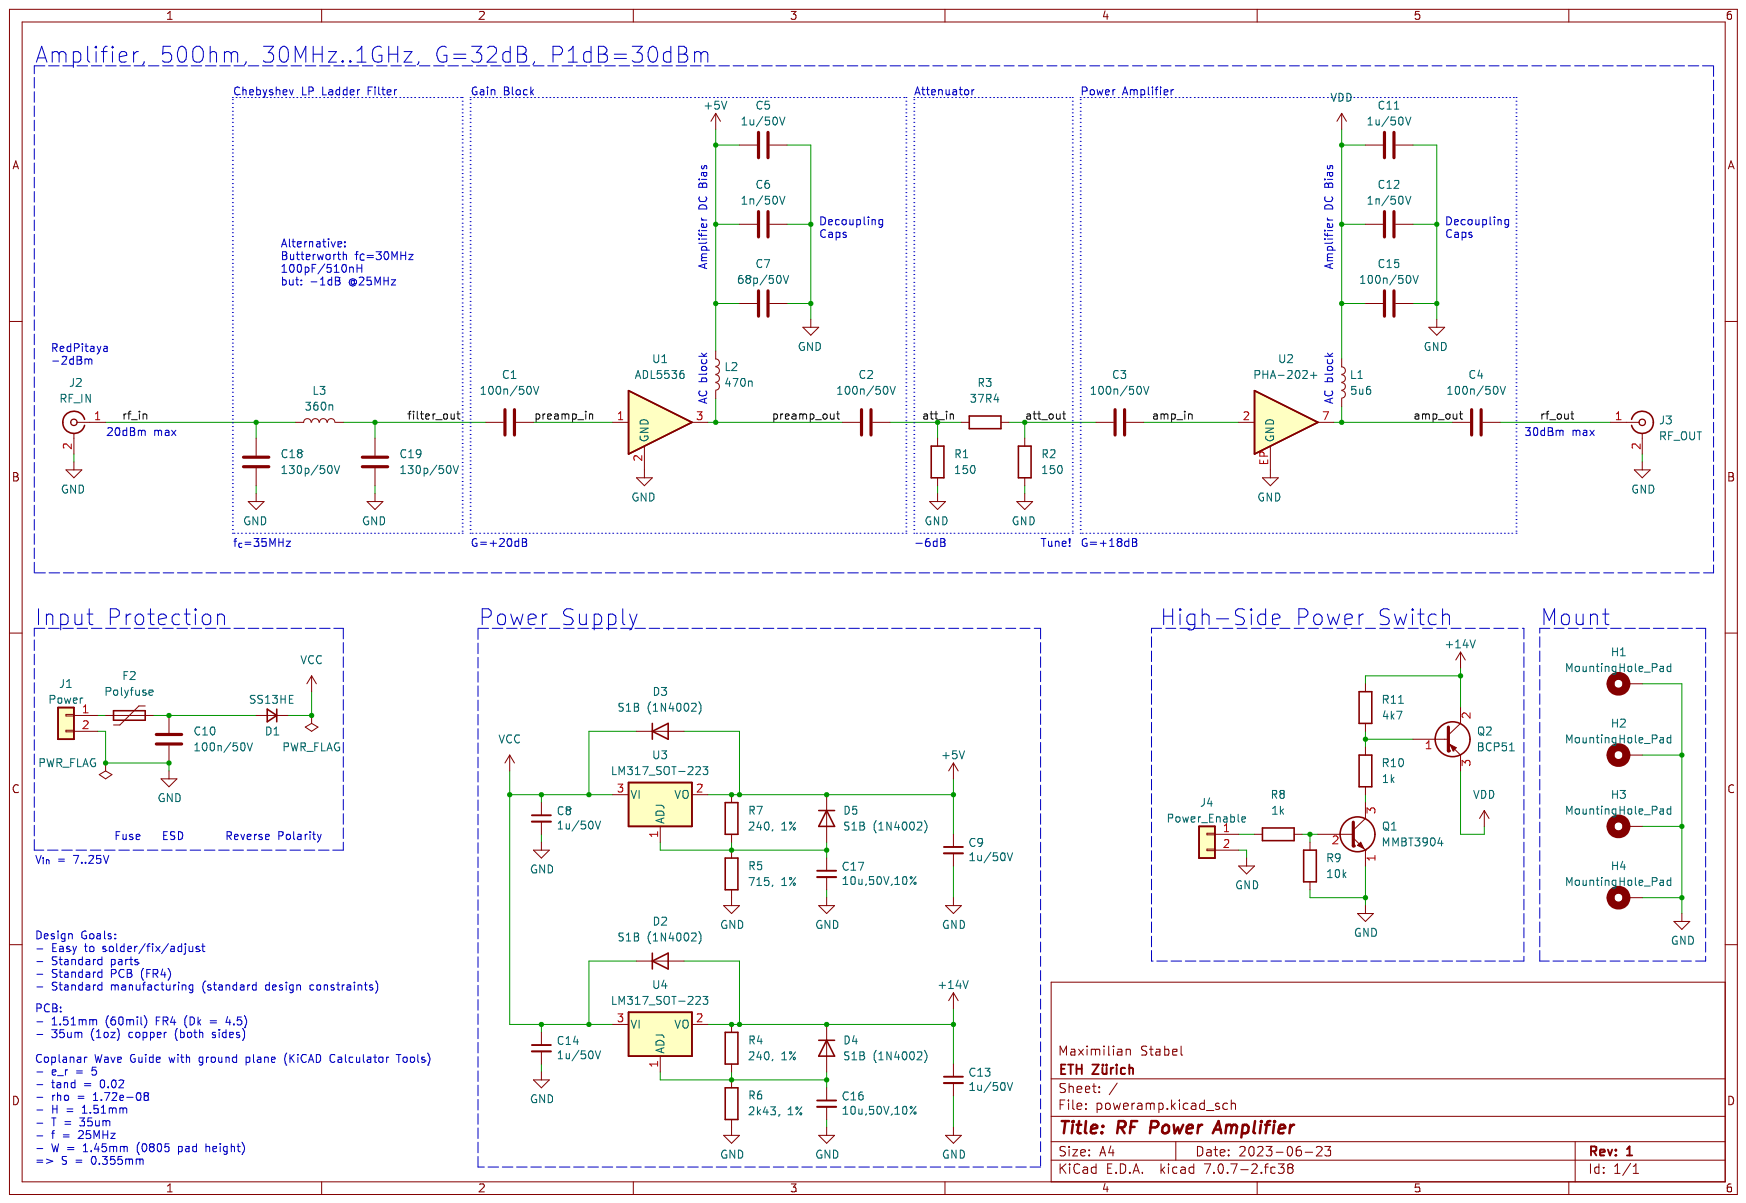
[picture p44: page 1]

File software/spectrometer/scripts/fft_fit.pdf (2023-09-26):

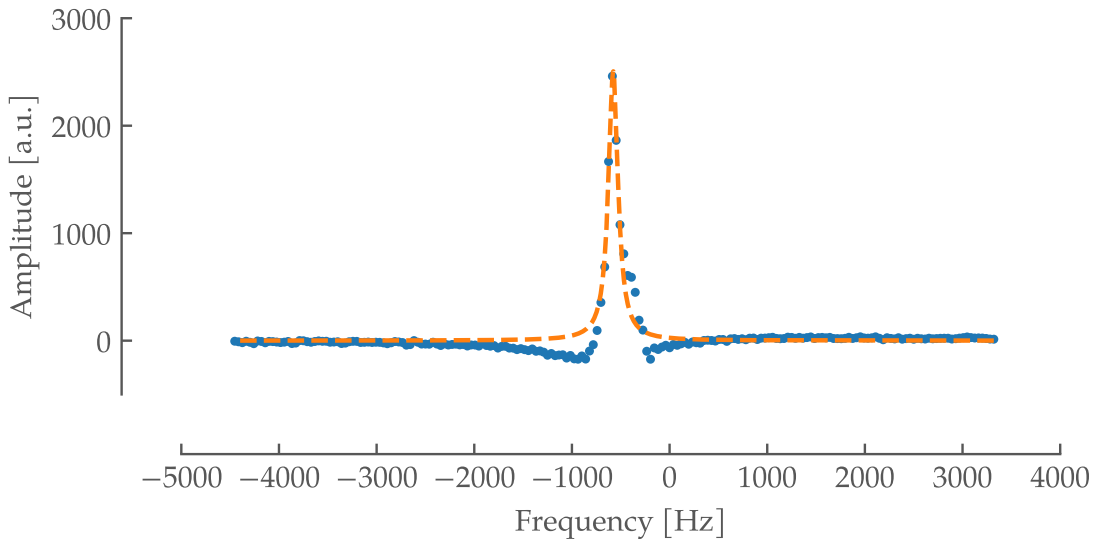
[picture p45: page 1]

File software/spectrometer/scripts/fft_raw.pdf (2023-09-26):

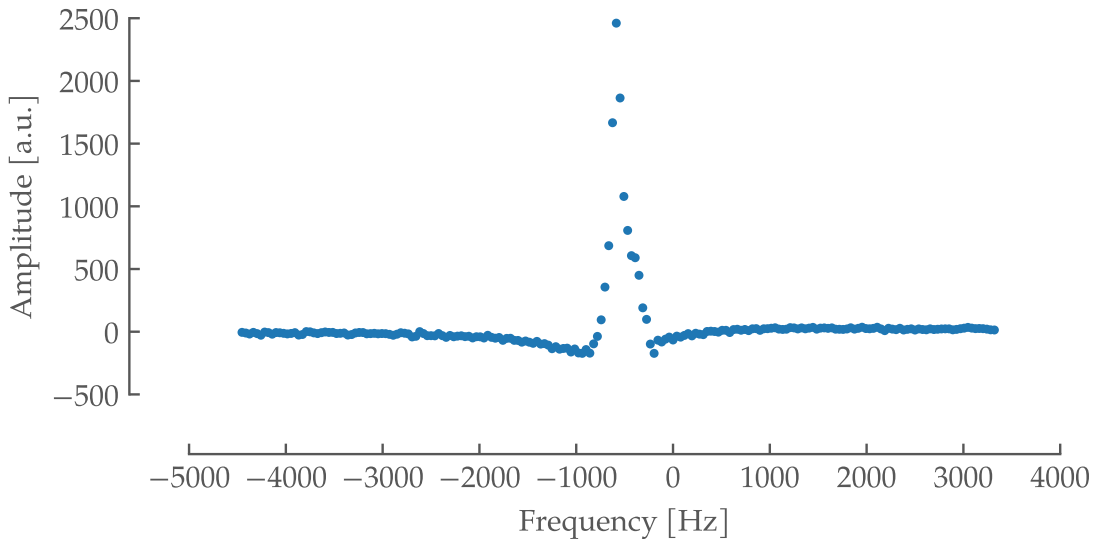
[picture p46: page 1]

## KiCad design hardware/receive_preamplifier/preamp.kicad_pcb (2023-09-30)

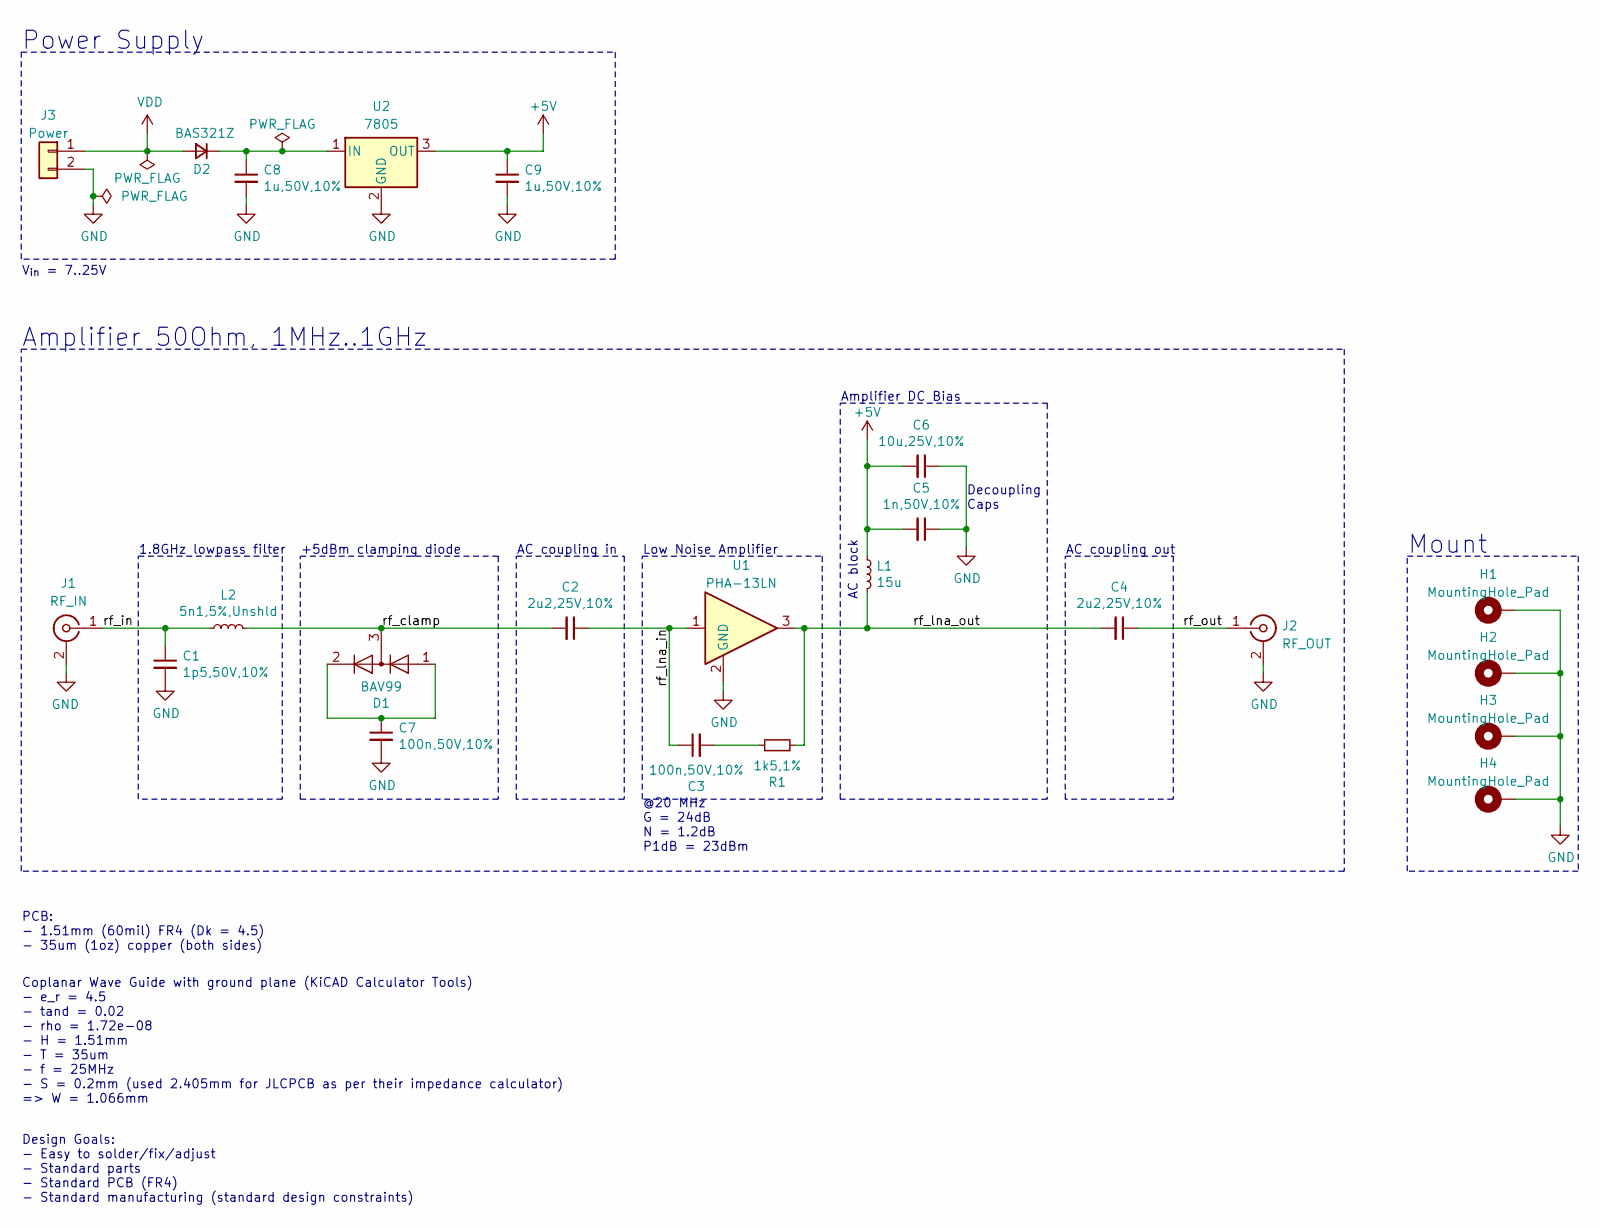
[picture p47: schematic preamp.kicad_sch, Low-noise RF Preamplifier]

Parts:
C1: 1p5,50V,10%; C_0805_2012Metric; MPN CC0805BRNPO9BN1R5; Mouser 603-CC805BRNPO9BN1R5
C2, C4: 2u2,25V,10%; C_0805_2012Metric; MPN CL21A225KAFNNNG; Mouser 187-CL21A225KAFNNNG
C3: 100n,50V,10%; C_0402_1005Metric_Pad0.74x0.62mm_HandSolder; MPN GRM155R71H104KE14D; Mouser 81-GRM155R71H104KE4D
C5: 1n,50V,10%; C_0805_2012Metric; MPN CL21B102KBANFNC; Mouser 187-CL21B102KBANFNC
C6: 10u,25V,10%; C_0805_2012Metric; MPN CL21A106KAYNNNG; Mouser 187-CL21A106KAYNNNG
C7: 100n,50V,10%; C_0805_2012Metric; MPN CL21B104KBCNNNC; Mouser 187-CL21B104KBCNNNC
C8, C9: 1u,50V,10%; C_0805_2012Metric; MPN CL21B105KBFNNNG; Mouser 187-CL21B105KBFNNNG
D1: BAV99; SOT-23; MPN BAV99; Mouser 583-BAV99
D2: BAS321Z; D_SOD-323_HandSoldering; MPN BAS321Z; Mouser 771-BAS321Z
H1, H2, H3, H4: MountingHole_Pad; MountingHole_2.2mm_M2_Pad_Via
J1: RF_IN; SMA_Molex_73251-1153_EdgeMount_Horizontal; MPN 142-0701-851; Mouser 530-142-0701-851
J2: RF_OUT; SMA_Molex_73251-1153_EdgeMount_Horizontal; MPN 142-0701-851; Mouser 530-142-0701-851
J3: Power; PinHeader_1x02_P2.54mm_Vertical; MPN 68491-102HLF; Mouser 649-68491-102HLF
L1: 15u; L_0805_2012Metric; MPN CV201210-150K; Mouser 652-CV201210-150K
L2: 5n1,5%,Unshld; L_0805_2012Metric; MPN 0805HT-5N1TJLC; Mouser 994-0805HT-5N1TJLC
R1: 1k5,1%; R_0402_1005Metric_Pad0.72x0.64mm_HandSolder; MPN RC0402FR-071K5L; Mouser 603-RC0402FR-071K5L
U1: PHA-13LN; SOT-89-3_Handsoldering; MPN PHA-13LN+; Mouser 139-PHA-13LN
U2: 7805; SOT-223-3_TabPin2; MPN UA78M05IDCYR; Mouser 595-UA78M05IDCYR

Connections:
+5V: C5.2, C6.2, C9.1, L1.1, U2.3 (OUT)
/rf_clamp: C2.2, D1.3 (K), L2.2
/rf_in: C1.1, J1.1 (In), L2.1
/rf_lna_in: C2.1, C3.1, U1.1
/rf_lna_out: C4.2, L1.2, R1.2, U1.3
/rf_out: C4.1, J2.1 (In)
GND: C1.2, C5.1, C6.1, C7.2, C8.2, C9.2, H1.1, H2.1, H3.1, H4.1, J1.2 (Ext), J2.2 (Ext), J3.2, U1.2 (GND), U2.2 (GND)
unnamed: C3.2, R1.1
unnamed: C7.1, D1.1 (K), D1.2 (A)
unnamed: C8.1, D2.1 (K), U2.1 (IN)
VDD: D2.2 (A), J3.1

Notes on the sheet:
Design Goals: - Easy to solder/fix/adjust - Standard parts - Standard PCB (FR4) - Standard manufacturing (standard design constraints)
Amplifier 50Ohm, 1MHz..1GHz
Amplifier DC Bias
V_{in} = 7..25V
+5dBm clamping diode
@20 MHz G = 24dB N = 1.2dB P1dB = 23dBm
AC block
AC coupling in
Low Noise Amplifier
Decoupling Caps
Power Supply
AC coupling out
1.8GHz lowpass filter
Mount
PCB: - 1.51mm (60mil) FR4 (Dk = 4.5) - 35um (1oz) copper (both sides)
Coplanar Wave Guide with ground plane (KiCAD Calculator Tools) - e_r = 4.5 - tand = 0.02 - rho = 1.72e-08 - H = 1.51mm - T = 35um - f = 25MHz - S = 0.2mm (used 2.405mm for JLCPCB as per their impedance calculator) => W = 1.066mm

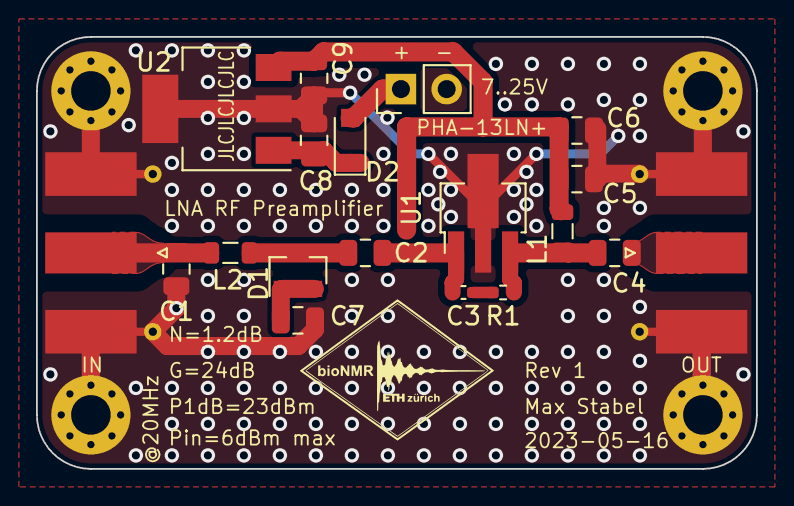
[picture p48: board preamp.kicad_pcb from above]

Board: 2 copper layers, 40.0 x 24.0 mm, 23 parts (0 on the bottom side), 11 nets.

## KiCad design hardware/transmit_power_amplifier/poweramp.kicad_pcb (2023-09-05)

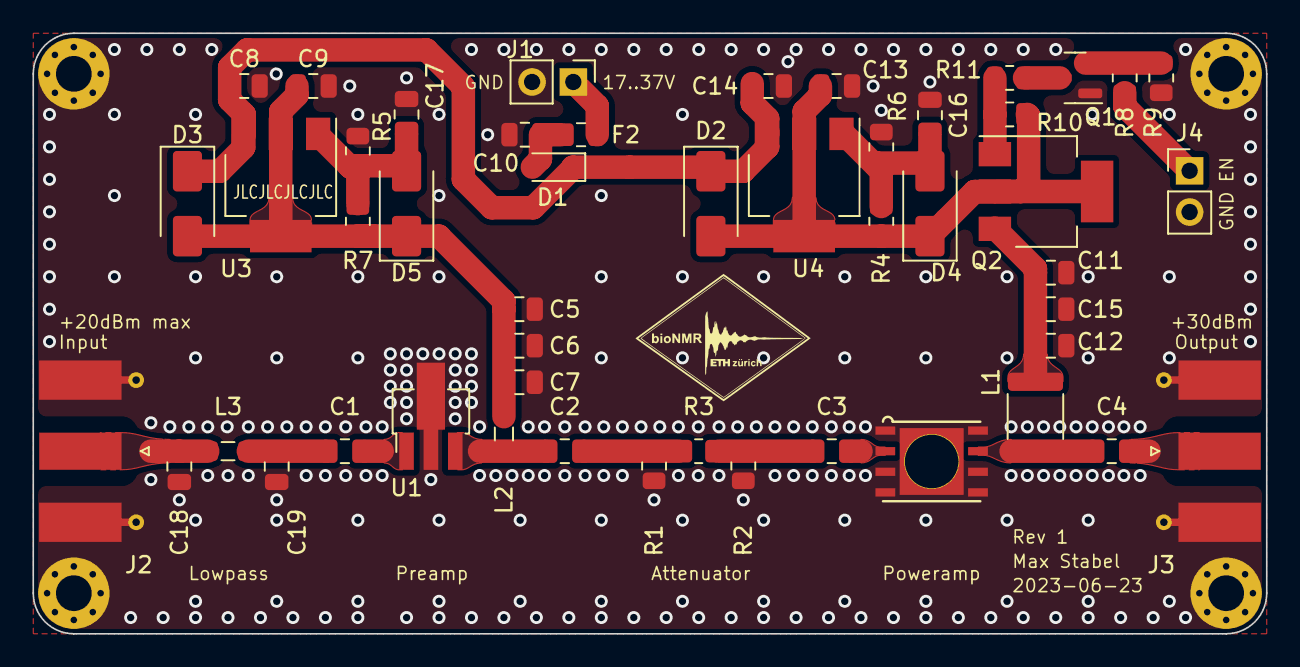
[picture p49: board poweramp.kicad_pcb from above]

Board: 2 copper layers, 76.0 x 37.0 mm, 53 parts (0 on the bottom side), 22 nets.

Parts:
C1, C2, C3, C4, C10, C15: 100n/50V; C_0805_2012Metric
C5, C11: 1u/50V; C_0805_2012Metric
C6, C12: 1n/50V; C_0805_2012Metric
C7: 68p/50V; C_0805_2012Metric
C8, C9, C13, C14: 1u,50V,10%; C_0805_2012Metric
C16, C17: 10u,50V,10%; C_0805_2012Metric
C18, C19: 130p/50V; C_0805_2012Metric
D1: SS13HE; D_SOD-323_HandSoldering
D2, D3, D4, D5: S1B (1N4002); D_SMA
F2: Polyfuse; Fuse_0805_2012Metric
H1, H2, H3, H4: MountingHole_Pad; MountingHole_2.2mm_M2_Pad_Via
J1: Power; PinHeader_1x02_P2.54mm_Vertical
J2: RF_IN; SMA_Molex_73251-1153_EdgeMount_Horizontal
J3: RF_OUT; SMA_Molex_73251-1153_EdgeMount_Horizontal
J4: Power_Enable; PinHeader_1x02_P2.54mm_Vertical
L1: 5u6; L_1812_4532Metric
L2: 470n; L_0805_2012Metric
L3: 360n; L_0805_2012Metric
Q1: MMBT3904; SOT-23
Q2: BCP51; SOT-223-3_TabPin2
R1, R2: 150; R_0805_2012Metric
R3: 37R4; R_0805_2012Metric
R4, R7: 240, 1%; R_0805_2012Metric
R5: 715, 1%; R_0805_2012Metric
R6: 2k43, 1%; R_0805_2012Metric
R8, R10: 1k; R_0805_2012Metric
R9: 10k; R_0805_2012Metric
R11: 4k7; R_0805_2012Metric
U1: ADL5536; SOT-89-3_Handsoldering
U2: PHA-202+; DL1636_HandSolder
U3, U4: LM317_SOT-223; SOT-223-3_TabPin2

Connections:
+5V: C5.1, C6.1, C7.1, C9.1, D3.2 (A), D5.1 (K), L2.1, R7.1, U3.2 (VO)
+14V: C13.1, D2.2 (A), D4.1 (K), Q2.2 (C), R4.1, R11.2, U4.2 (VO)
/amp_in: C3.2, U2.2
/amp_out: C4.1, L1.2, U2.7
/att_in: C2.2, R1.1, R3.1
/att_out: C3.1, R2.1, R3.2
/filter_out: C1.1, C19.2, L3.2
/preamp_in: C1.2, U1.1
/preamp_out: C2.1, L2.2, U1.3
/rf_in: C18.2, J2.1 (In), L3.1
/rf_out: C4.2, J3.1 (In)
GND: C5.2, C6.2, C7.2, C8.2, C9.2, C10.1, C11.2, C12.2, C13.2, C14.2, C15.2, C16.2, C17.2, C18.1, C19.1, H1.1, H2.1, H3.1, H4.1, J1.2, J2.2 (Ext), J3.2 (Ext), J4.2, Q1.1 (E), R1.2, R2.2, R5.2, R6.2, R9.1, U1.2 (GND), U2.1 (EP), U2.3 (EP), U2.4 (EP), U2.5 (EP), U2.6 (EP), U2.8 (EP), U2.EP (GND)
unnamed: C10.2, D1.2 (A), F2.2
unnamed: C16.1, D4.2 (A), R4.2, R6.1, U4.1 (ADJ)
unnamed: C17.1, D5.2 (A), R5.1, R7.2, U3.1 (ADJ)
unnamed: F2.1, J1.1
unnamed: J4.1, R8.1
unnamed: Q1.2 (B), R8.2, R9.2
unnamed: Q1.3 (C), R10.1
unnamed: Q2.1 (B), R10.2, R11.1
VCC: C8.1, C14.1, D1.1 (K), D2.1 (K), D3.1 (K), U3.3 (VI), U4.3 (VI)
VDD: C11.1, C12.1, C15.1, L1.1, Q2.3 (E)

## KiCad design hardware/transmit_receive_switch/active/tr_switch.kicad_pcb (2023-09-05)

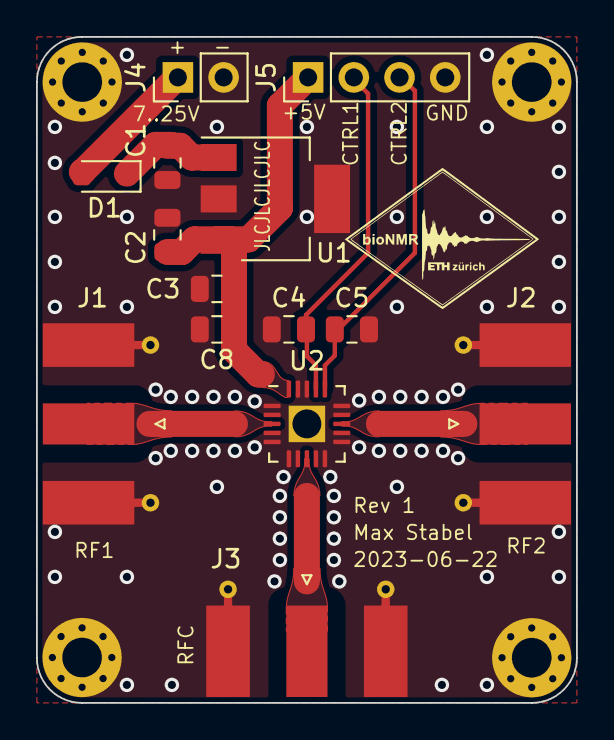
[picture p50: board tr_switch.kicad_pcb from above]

Board: 2 copper layers, 30.0 x 37.0 mm, 18 parts (0 on the bottom side), 9 nets.

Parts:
C1, C2: 1u,50V,10%; C_0805_2012Metric
C3: 1u/50V; C_0805_2012Metric
C4, C5: 200p/50V; C_0805_2012Metric
C8: 100n/50V; C_0805_2012Metric
D1: BAS321Z; D_SOD-323_HandSoldering
H1, H2, H3, H4: MountingHole_Pad; MountingHole_2.2mm_M2_Pad_Via
J1: RF1; SMA_Molex_73251-1153_EdgeMount_Horizontal
J2: RF2; SMA_Molex_73251-1153_EdgeMount_Horizontal
J3: RFC; SMA_Molex_73251-1153_EdgeMount_Horizontal
J4: Power; PinHeader_1x02_P2.54mm_Vertical
J5: Control; PinHeader_1x04_P2.54mm_Vertical
U1: 7805; SOT-223-3_TabPin2
U2: QPC6324; QFN-20-1EP_4x4mm_P0.5mm_EP2x2mm_HandSolder

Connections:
+5V: C2.1, C3.1, C8.1, J5.1, U1.3 (OUT), U2.20
/VDD_p: C1.1, D1.1 (K), U1.1 (IN)
/rf1: J1.1 (In), U2.3
/rf2: J2.1 (In), U2.13
/rfc: J3.1 (In), U2.8
GND: C1.2, C2.2, C3.2, C4.1, C5.1, C8.2, H1.1, H2.1, H3.1, H4.1, J1.2 (Ext), J2.2 (Ext), J3.2 (Ext), J4.2, J5.4, U1.2 (GND), U2.1, U2.2 (GND), U2.4 (GND), U2.5 (GND), U2.6 (GND), U2.7 (GND), U2.9 (GND), U2.10 (GND), U2.11 (GND), U2.12 (GND), U2.14 (GND), U2.15 (GND), U2.18 (GND), U2.19 (GND), U2.21 (GND)
unnamed: C4.2, J5.2, U2.17
unnamed: C5.2, J5.3, U2.16
VDD: D1.2 (A), J4.1

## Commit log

2023-04-03 Add magnet specifications
    [2023-01-03 ETH 0.6T active shim Matrix and Pinouts.xlsx]
2023-04-04 Add 3D Printing instructions
2023-04-04 Add Andrew McDowell's rf probe holder
    [230403-rf_probe_holder_innards_7-5_andrew_mcdowell.stl]
2023-04-04 Add more complete map data for shimmed magnet
    [230403-magnet_data_map_andrew_mdowell.xlsx]
2023-04-04 Add Rf probe holder draft print gcode
2023-04-04 Add Andrew McDowell's rf probe holder prusa project
    [230403-rf_probe_holder_innards_7-5_andrew_mcdowell.3mf]
2023-04-04 Add 230403-probe_holder_v1.scad incl. print files
    [230403-probe_holder_v1.3mf, 230403-probe_holder_v1.scad, 230403-probe_holder_v1.stl]
2023-04-05 Add more NMR background literature
    Add McDowell Patents and publications on active and passive shimming.
    Also add McDowell pubication on high-order shims for small dipole NMR
    magnets
    [2023-01-03 ETH 0.6T active shim Matrix and Pinouts.xlsx, 230403-magnet_data_map_andrew_mdowell.xlsx]
2023-04-05 Auto format probe holder v1
    [230403-probe_holder_v1.scad]
2023-04-05 Add probe_holder_v1 printed gcode un MK3S printer
2023-04-06 Fix folder name
    [2023-01-03 ETH 0.6T active shim Matrix and Pinouts.xlsx, 230403-magnet_data_map_andrew_mdowell.xlsx]
2023-04-13 Add first rf coil documentation
    [230403-probe_holder_v1.3mf, 230403-probe_holder_v1.scad, 230403-probe_holder_v1.stl, 230403-rf_probe_holder_innards_7-5_andrew_mcdowell.3mf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]
2023-04-17 Fix typo in filename
    [230403-magnet_data_map_andrew_mcdowell.xlsx]
2023-04-21 Add full power test
2023-04-28 Move current source to workspace
2023-05-02 Add reference to current source design options
2023-05-22 Add further tx/rx amp research to readmes
    [230510-shopping_list.ods]
2023-05-22 Add RX LNA Preamp KiCAD design
    [142-0701-851.stp, preamp.kicad_pcb, preamp.kicad_sch]
2023-05-23 Order at JLCPCB with modified rf clearances
    [preamp.kicad_pcb, preamp.kicad_sch]
2023-05-24 Move LNA into own folder
    [142-0701-851.stp, preamp.kicad_pcb, preamp.kicad_sch]
2023-05-30 Restructure LNA/PA/Switch READMEs
    [230510-shopping_list.ods]
2023-05-31 Fix rx lna preamp production output settings
    [preamp.kicad_pcb]
2023-05-31 Update current driver/amp readmes
2023-05-31 Add RF/Circuits literature
2023-06-02 Add LNA board measurements
2023-06-07 Add Amplifier clamping @25MHz
2023-06-07 RP protection clamping pictures
2023-06-08 Update power amp considerations README.md
2023-06-14 Add enable switch to poweramp
    [poweramp.kicad_pcb, poweramp.kicad_sch]
2023-06-14 Add various diodes to clamping_diodes simulation
2023-06-23 Update file permissions, rf_switch and poweramp
    [142-0701-851.stp, 2023-01-03 ETH 0.6T active shim Matrix and Pinouts.xlsx, 230403-magnet_data_map_andrew_mcdowell.xlsx, 230403-probe_holder_v1.3mf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]
2023-06-28 Add power supply channel ltspice simulation
2023-06-28 Remove gerber outputs
    [tr_switch-CuBottom.gbr, tr_switch-CuTop.gbr, tr_switch-EdgeCuts.gbr, tr_switch-MaskBottom.gbr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]
2023-06-28 Get TR-Switch Rev 1 ready for ordering
    [tr_switch.kicad_sch]
2023-06-28 Get poweramp Rev 1 ready for ordering
    [poweramp.kicad_pcb, poweramp.kicad_sch]
2023-06-28 Move current source simulations in subfolder
2023-07-06 Update 32-Channel Current Source Rev 1
    [32-channel_current_source.kicad_sch, 8-channel_current_source.kicad_sch, CT3151-0.STEP, CT3151-2.STEP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]
2023-07-19 Update 32-channel_current_source pcb
2023-07-20 Include first water/coil measurements
    [20230720-find_peaks_max_amplitudes.csv, 20230720-find_peaks_pulse_lengths.csv]
2023-08-04 Finish Rev 1 of the 32-channel current supply
    [1590Z150.stp, 32-channel_current_source.FCStd, 32-channel_current_source.kicad_sch, 4610-6050.stp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]
2023-08-04 Move python spectrometer interface to own folder
    [20230720-find_peaks_max_amplitudes.csv, 20230720-find_peaks_pulse_lengths.csv]
2023-08-09 Restructure repository
    [142-0701-851.stp, 1590Z150.stp, 2023-01-03 ETH 0.6T active shim Matrix and Pinouts.xlsx, 20230720-find_peaks_max_amplitudes.csv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]
2023-08-15 Add circuitikz to tex package
2023-08-20 Remove processed data from repo
    [20230720-find_peaks_max_amplitudes.csv, 20230720-find_peaks_pulse_lengths.csv]
2023-08-28 Add lambda to decay print
2023-08-28 Add simulated Toluene data
    Simulated at B_0 = 25MHz with a linewidth of 50Hz with MestReNova 14.3.3
    [toluene_simulation_25MHz_field_50Hz_linewidth.csv]
2023-08-28 Crop toluene simulation data
    [toluene_simulation_25MHz_field_50Hz_linewidth.csv]
2023-08-28 Fix toluene simulation data format
    [toluene_simulation_25MHz_field_50Hz_linewidth.csv]
2023-09-04 Add poweramp assembly bom
2023-09-05 Add 3D models for 3D render
    [73251-1153.stp, PHA-202+.stp, poweramp.kicad_pcb, poweramp.kicad_sch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]
2023-09-07 Add 3D render for 32-channel-current-source
2023-09-08 Add simple nmrglue powered peak picking, fitting and spectrum simulation
2023-09-10 Add combined LNA/attenuator/filter/protection osci measurement
2023-09-10 Record 25MHz signal from signal generator
    10mVpp with 30dB attenuator, recorded at 25.001MHz with a 320kHz sample rate
2023-09-19 WIP: Materials & Methods
2023-09-27 Expand poweramp section
2023-09-30 Fix lna feedback loop
    [preamp.kicad_pcb, preamp.kicad_sch]
2023-09-30 Invert graphs for better printing in thesis
2023-09-30 Edit current source simulation output to be more legible
2023-09-30 Add current source chapter to thesis

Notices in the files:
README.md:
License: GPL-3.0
